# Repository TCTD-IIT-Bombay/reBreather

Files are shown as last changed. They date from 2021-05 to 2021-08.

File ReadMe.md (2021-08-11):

# Overview

There is currently an acute shortage of medical grade oxygen in large parts of India, as a consequence of a big surge in the number of critical Covid-19 cases, as well as logistical challenges associated with the oxygen supply chain. Several past and current students and research staff members of  [IIT Bombay](https://www.iitb.ac.in) (affiliated with [Tata Centre for Technology and Design](http://www.tatacentre.iitb.ac.in/), [Chemical Engineering](https://www.che.iitb.ac.in), and [Nex Robotics](http://www.nex-robotics.com)) have come together to attempt solutions which focus on reducing O<sub>2</sub> wastage, from the patient consumption perspective.

We have built a prototype breathing device called reBreather, which can minimize the wastage of oxygen when a patient is put on assisted breathing with supplemental oxygen via O<sub>2</sub> cylinders or centralised O<sub>2</sub> supply in hospitals.  Our reBreather prototype is a semi-closed circular breathing system that would allow patients to breathe in unused exhaled oxygen which has been filtered to remove CO<sub>2</sub>.

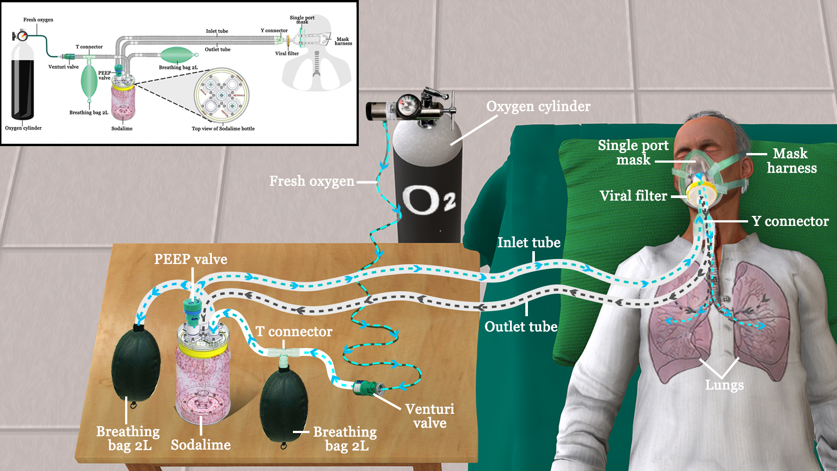
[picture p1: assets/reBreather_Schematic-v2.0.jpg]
reBreather Flow


The hardware design is available in the public domain under the Creative Commons 4.0 license ([CC BY-SA 4.0](https://creativecommons.org/licenses/by-sa/4.0/)) so that others can replicate the design. We urge individuals and makers communities across the world to come forward and 
1. Help assemble copies of the prototype, and 
2. Contribute design improvements or customizations, including for better scalability. 

This design has currently been tested on healthy volunteers: our objective in releasing this design now is to document the science behind the technique and test that it works in a practical context, and potentially help mitigate wastage of O<sub>2</sub> at a time when there is a heavy demand for it.

We have added explanations on how the reBreather works and on how to build a unit, with detailed pictures and instructions. Vendor and pricing details of the parts we have used in this design have also been provided. We have sourced these with relative ease in Mumbai; you may find cheaper - and better - alternatives for these items. Feel free to let us know if there are ways by which you can help us in improving the design or documentation, or with better vendor connections.  

# ⚠️ Disclaimers

We make no representation as to the operability and in particular, the fitness, safety, and efficacy of this solution. This prototype has been designed with inputs from experts with Anesthesiology and Intensive Care backgrounds, but at this time has only been informally tested on healthy volunteers. It has not been clinically tested in a controlled fashion and approved for routine use. We release this design into the public domain with the intent of encouraging further research and testing, towards improving the design. We strongly recommend the following:

- This prototype should only be tested and used under the close supervision of a trained medical professional, familiar with methods of alleviating respiratory distress.
- Flow settings should be modulated by systematic monitoring over time, by a professional, of a patient's FiO<sub>2</sub> (fraction of inspired oxygen), CO<sub>2</sub> percentage, and the effort of breathing.
- The prototype relies on the soda lime changing colour as its CO<sub>2</sub> absorption capacity is exhausted; its appearance must be frequently monitored, and the exhausted absorbent replaced with fresh soda lime in a timely fashion. 

# How does reBreather work?

In a normal open-loop oxygen-breathing system, a mask is directly connected to the oxygen supply at a particular flow rate. During inhalation, the human respiratory system takes in this oxygen stream, in some cases along with atmospheric air. In the exhalation cycle, the person breathes out unutilized gases as well as the CO<sub>2</sub> generated as a by-product of metabolism. A healthy person normally breathes in 5 liters per minute (L/min) of air. This corresponds (assuming air has ~20% O<sub>2</sub>) to about 1 L/min of O<sub>2</sub> being inhaled; of this, ~0.25 L/min of O<sub>2</sub> is consumed.  Critically ill Covid-19 patients can receive up to 50 L/min of O<sub>2</sub> using a high-flow nasal cannula and mask combination. Consequently, during one open loop breathing cycle for such patients, most of the oxygen is lost back to the atmosphere.

A rebreather is a closed (or semi-closed) loop system that helps the user to rebreathe the unused oxygen that they have just exhaled. To do this, rebreathers have a section that helps remove the CO<sub>2</sub> in the exhaled air thereby preventing an increase in the CO<sub>2</sub> concentration in the closed-loop system. The amount of oxygen absorbed by the user is replenished by a fresh supply of oxygen into the closed-loop. This concept has extensively been used in underwater diving breathing devices. Those designs are significantly more complex in practice, however, and have a fully closed loop system with air sensors measuring concentrations of O<sub>2</sub> and adjusting the input oxygen flow accordingly.

It will be beneficial to recirculate the unused oxygen, especially when the latter is in short supply.  Releasing a lot of oxygen results in the oxygen concentration going up, especially in closed spaces.  This could be a reason for the increased fire incidence in hospitals, during the current pandemic.  The solution presented in this work is an attempt to address this problem, as explained next.

Our solution (called reBreather) is a semi-closed circular breathing system. We have an inlet section which pumps in fresh oxygen from an oxygen cylinder or a centralised oxygen system in hospitals. The oxygen flow rate is set on the cylinder with a flow meter. An adjustable venturi valve is given at the input to allow for external air to be automatically pulled in based on the desired oxygen flow rate. A one port mask is attached to the patient; it has a Y connector which connects to a bacterial/viral filter at one end. At the other end, the Y connector has an inlet for incoming air and an outlet for exhaled air. Flow directions are regulated by using one-directional valves.  The exhaled air is fed to a container which contains medical-grade soda lime which selectively absorbs CO<sub>2</sub> and allows the rest of the air to pass through to the inlet section of our system.

Medical grade soda lime changes colour once it has exhausted its capability to absorb CO<sub>2</sub>. There are different indicator dyes in use, with colour change combinations varying across manufacturers and brands (for example, pink (fresh) to white (exhausted), or white (fresh) to violet (exhausted), etc.). It is important to note that a soda lime colour change must be promptly attended to: at this time we recommend that it be replaced with a fresh batch of soda lime towards continuous use of the device: an elevation in the CO<sub>2</sub> concentration in the rebreather circuit would be harmful to the patient.

Approximate calculations of unit performance are provided below for various scenarios. These are O<sub>2</sub> utilization estimates for a single patient, and assuming that a cylinder holds 7800 L of pure O<sub>2</sub>. The closed loop design assumes 10% purge of the recirculating stream, per cycle, with an equivalent introduction of fresh O<sub>2</sub>. Units are in cylinders/day.(Detailed calculations are available in a separate [pdf file](./assets/Estimated_Oxygen_Savings.pdf)).

| Scenario / cylinders per patient per day                                       | Open loop  | Closed loop  with reBreather |
|------------------------------------------------|:----------:|:----------------------------:|
| Nasal Cannula 6 L/min O<sub>2</sub> | 1.1 | 0.28 |
| Nonrebreathing mask (NRM), 15 L/min O<sub>2</sub> | 2.8 | 0.44 |
| High Flow Nasal Cannula (HFNC), 50 L/min O<sub>2</sub> | 9.2 | 1.09 |

# FAQs

1. Can I build this device based on the parts mentioned? \
Yes, you can. However, (as explained above) it should be used solely under the supervision of a trained medical professional. 

2. Is the design open source? \
Yes. The entire hardware design is made available in the public domain under a Creative Commons 4.0 license ([CC BY-SA 4.0](https://creativecommons.org/licenses/by-sa/4.0/)). This design is accessible on our [GitHub page](https://github.com/TCTD-IIT-Bombay/reBreather). 

3. How can I help? \
You can also help us in testing the design, and by suggesting modifications to further improve its performance and manufacturability. Talk to doctors and give us their inputs. There are several elements in the design which can be further optimised. Our primary focus during this initial build cycle has been on establishing efficacy of the design. We have, to a lesser extent, focussed on incorporating off the shelf branded parts which we think anyone else would also be able to source locally. Feel free to fork the project, edit it and create pull requests if you have a way to make the design better or have an alternate design which will work.
You can also help us (and others) by finding better vendor sources in your city.     

4. What is the current status of the project?  \
(As of Aug 11 2021:) We are releasing version v2.0 of the reBreather prototype design. This design has been tested on a healthy team member who was hooked up to a patient monitoring device, under the supervision of clinical specialists.  His vital signs, breathing rate, inhalation & exhalation O<sub>2</sub> /CO<sub>2</sub>  levels were monitored. \
At a low O<sub>2</sub>  input flow rate of 1 L/min, the volunteer was able to maintain normal breathing patterns with O<sub>2</sub>  and CO<sub>2</sub>  levels well within limits. We were able to establish that CO<sub>2</sub>  is continuously being removed from the system. \
A few changes were made on the v1.0 prototype design which includes adding another breathing bag after the venturi valve, changes in the design of the jar lid and the adapters to have a more efficient pathway to flow. Iterative experiments were also conducted on soda lime to test the amount of C0<sub>2</sub> absorbed and how to make it more long lasting. This version of prototype is now undergoing clinical trials.
There are further modifications that we are working on to make the designs better and easier to manufacture. We will keep updating the Hardware design folder with design variations as and when these changes are introduced.

5. How can I add modifications to the design? \
We urge you to contribute back any design updates. You can fork this  project (learn how to do so [here](https://www.youtube.com/watch?v=_NrSWLQsDL4)) and create a copy. Now create a new subfolder inside the Hardware Designs folder with the latest version number. The versioning scheme (**vX.Y**) is as follows: \
v1.0 --> Original Design \
v2.0 --> Updated Design \
For major modifications to a particular design, increment X by 1 (eg. v2.0, v3.0). If you make a minor edit to a particular design, increment Y by 1, from the base design you modified (eg. v1.2, v1.4, v2.3).\
In this new folder, make sure you have the following files and folders (For reference check the original v1.0 folder) 
- *Hardware Parts Explained.pdf* --> Explaining each and very part of your design with pictures 
- *Assembly Steps.pdf* --> Detailed steps on how you will put this together 
- *Bill of Materials* --> Bill of materials file containing the parts to be purchased/3D printed/Lasercut/moulded 
- *Mechanical CAD Folder* --> Containing editable files for the community along with the 3D printed files(if any)\
Detailing the changes made and why you think it is better. Add a picture of the full setup. List potential issues you find in the version you build so that others can help suggest improvements. 
Once the folder along with the above contents are made. Add the final picture of your setup to the main ReadMe file in the Hardware Designs folder with your version number so that someone can find the full design evolution in one page. \
Please submit a [pull request](https://docs.github.com/en/github/collaborating-with-issues-and-pull-requests/about-pull-requests) with your changes. We will review the changes and add to the Github project page.
6. How can I contact the team?  \
Drop us a mail at rebreather@tctd.iitb.ac.in

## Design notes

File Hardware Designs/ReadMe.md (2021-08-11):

# How to contribute to this project? 

We urge you to contribute and make the published designs better. You can fork this project(Learn [here](https://www.youtube.com/watch?v=_NrSWLQsDL4)) and create a copy of this project. Now create a new folder on the *Hardware Designs* folder with the latest version number. 

The versioning scheme (**vX.Y**) is as follows: 

v1.0 --> Original Design 
v2.0 --> Updated Design

For major modifications to a particular design, increment X by 1 (eg. v2.0, v3.0). If you make a minor edit to a particular design, increment Y by 1, from the base design you modified (eg. v1.2, v1.4, v2.3). 
In this new folder, make sure you have the following files and folders (For reference check the original v1.0 folder) 
- *Hardware Parts Explained.pdf* --> Explaining each and very part of your design with pictures 
- *Assembly Steps.pdf* --> Detailed steps on how you will put this together 
- *Bill of Materials* --> Bill of materials file containing the parts to be purchased/3D printed/Lasercut/moulded 
- *Mechanical CAD Folder* --> Containing editable files for the community along with the 3D printed files(if any) 
- *ReadMe.md* file --> Detailing the changes made and why you think it is better. Add a picture of the full setup. List potential issues you find in the version you build so that others can help suggest improvements. 

Once the folder along with the above contents are made. Add the final picture of your setup to the this ReadMe file towards the end in the Hardware Designs folder with your version number so that someone can find the full design evolution in one page. 

Please submit a [pull request](https://docs.github.com/en/github/collaborating-with-issues-and-pull-requests/about-pull-requests) with your changes. We will review the changes and add to the Github project page.

# Different Designs

### ***v1.0***

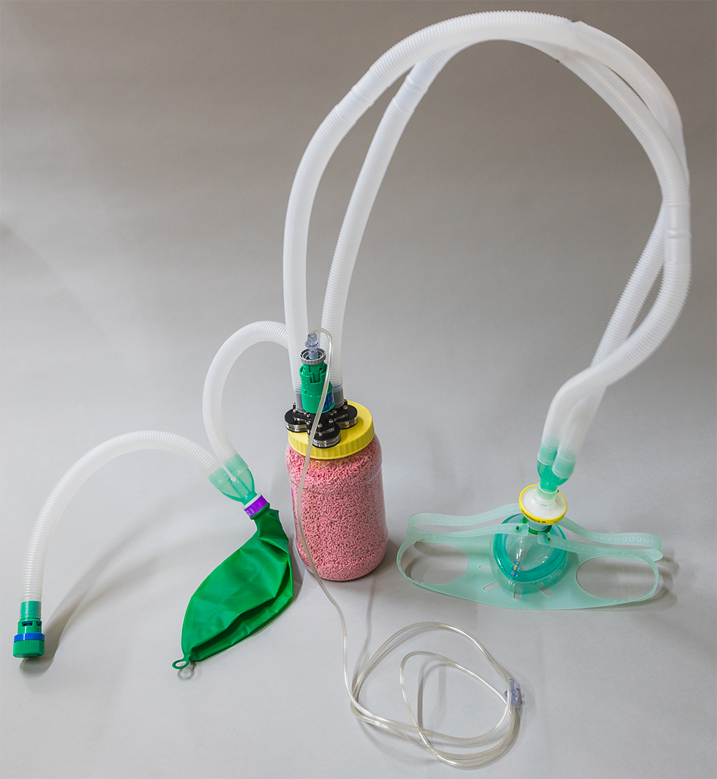
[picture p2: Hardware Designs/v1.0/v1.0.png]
v1.0


### ***v2.0***

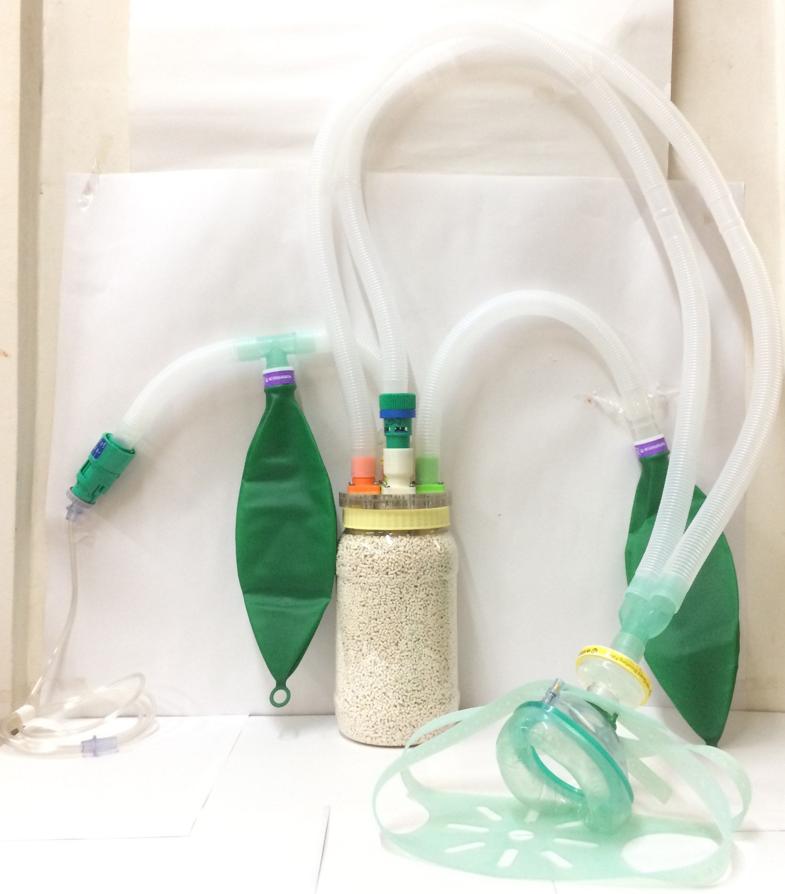
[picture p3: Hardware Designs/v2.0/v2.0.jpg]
v2.0


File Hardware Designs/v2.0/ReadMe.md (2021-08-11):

# Updated Design

The initial design was tested and a few changes were made, making the device more efficient and safe than the previous design. The changes will be mentioned below.

The usage of soda lime was also tested to bring out the maximum efficiency. Iterative experiments were carried out, by emulating the exhaled gas of a person with a CO<sub>2</sub> supplied to a container having the same amount of soda lime. The details of the experiment and the outcome is mentioned in the directory 'Sodalime'.

## Modifications in Design
- The valve have been brought out from the bottle lid, which allows easy replacement.
- An additional breathing bag is added after the venturi valve
- The PEEP outlet is coupled with exhalation port before entering the bottle to save wastage and better use of soda lime

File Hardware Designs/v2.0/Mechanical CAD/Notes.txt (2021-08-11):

Modification proposed:
1.Valve have been brought out from the bottle lid, allows easy replacement
2.Additional breathing bag to be added after venturi valve
3.It is better to use fixed venturi over adjustable venturi
4.Peep outlet is couple with exhalation port before entring the bottle to save wastage and better use of soda lime

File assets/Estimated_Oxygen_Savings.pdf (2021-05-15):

## Estimated O2 Savings by reBreather

The advantage of the Closed-Circuit system comes from the significant difference between the volume of O2 a patient with respiratory distress inhales and the actual volume of O2 the body picks up.

For reference, a healthy person breathes in ~5L/min of air (80% N2, 20% O2) which corresponds to ~1L/min of O2. Of this 1L/min inhaled, the healthy human body picks up only about
250mL/min [1] or 0.25L/min of O2. Hence the remaining 750mL/min of O2 is exhaled out unused and is lost to the environment. This O2 wastage can be more dramatic for ARDS patients: Covid-19 patients in intensive care can be given 50 L/min of O2 with only 1-1.5 L/min actually being utilized.

In a closed-circuit system, this lost oxygen is captured and recycled within the system. This allows the caregiver to send in fresh Oxygen only to make up for the O2 that is actually taken up by the human body.

A comparison of the number of cylinders consumed by a single patient when using non-closed-circuit systems like NRM/HFNO etc., versus our closed-circuit design is shown in the table below. The calculations for each of those numbers are shared after.

Scenarios | Open Loop (cylinders/day) | Closed Loop (10% purge) cylinders/day
Nasal Cannula, 6L/min* | 1.1 | ~0.28 (74% ↓)
Nonrebreathing mask, 15L/min* | 2.8 | ~0.44 (84%↓)
High Flow Nasal Cannula (HFNC), 50L/min* | 9.2 | ~1.09 (89%↓)

*Cylinder consumption shown for 1 patient

### 1 cylinder = 7800L of pure O2

## Scenarios:

### 1) Mild COVID patient treated at low-flow [6L/min O2] (Nasal Cannula)

Actual O2 Uptake by the body = 0.5L/min (assumed)

Open Loop:
O2 consumption from cylinder [L/min] = 6*60*24 = 8,640 L/day ~ 1.11 cyl/day

Closed Loop:
O2 consumption from cylinder [L/min] = 0.5*60*24 = 720 L/day ~ 0.09 cyl/day (without purge).
With 10% purge through a PEEP valve, this becomes 0.278 cyl/day.

### 2) Serious COVID Patient treated at 15L/min O2 (Nonrebreathing mask)

Actual O2 Uptake by the body = 1L/min (assumed)

Open Loop:
O2 consumption from cylinder [L/min] = 15*60*24 = 21,600 L/day ~ 2.77 cyl/day

Closed Loop:
O2 consumption from cylinder [L/min] = 1*60*24 = 1,440 L/day ~ 0.2 cyl/day. (without purge).
With 10% purge through a PEEP valve, this becomes 0.445 cyl/day.

### 3) Very Serious COVID Patient treated at 50L/min O2 (High flow nasal oxygen)

Actual O2 Uptake by the body = 1.5L/min (assumed)

Open Loop:
O2 consumption from cylinder [L/min] = 50*60*24 = 72,000 L/day ~ 9.23 cyl/day

Closed Loop:
O2 consumption from cylinder [L/min] = 1.5*60*24 = 2,160 L/day ~ 0.3 cyl/day (without purge).
With 10% purge through a PEEP valve, this becomes 1.09 cyl/day.

## References

[1] Leach RM, Treacher DF. The relationship between oxygen delivery and consumption. Dis Mon. 1994 Jul;40(7):301-68. PMID: 8020386.

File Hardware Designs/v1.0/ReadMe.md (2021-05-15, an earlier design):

# Initial Design

The initial design was done keeping prototyping time to a bare minimum and our goal was to document the science behind the technique and that it can actually work in real life. 

This design has been tested on a healthy team member who was hooked up to a patient monitoring device, under the supervision of clinical specialists.  His vital signs, breathing rate, inhalation & exhalation O<sub>2</sub> CO<sub>2</sub>  levels were monitored.

At a low O<sub>2</sub>  input flow rate of 1 L/min, the volunteer was able to maintain normal breathing patterns with O<sub>2</sub>  and CO<sub>2</sub>  levels well within limits. We were able to establish that CO<sub>2</sub>  is continuously being removed from the system.

## Known Issues
- The absorption process of C0<sub>2</sub> by sodalime is an exothermic reaction and the bottle will get warm during the process. We also tried pushing a large flow rate of pure C0<sub>2</sub> into the bottle and we did find that the PET bottle we used has a chance to get warped due to the heat. Potential alternatives are to pursue with thicker(2-3mm) acrylic tubes which has a higher deformation temperature. 
- The unidirectional valves do contain quite a number of parts which isn't that optimal for scalable designs. This is making the assembly process longer. We are working on simplifying the valve design significantly.

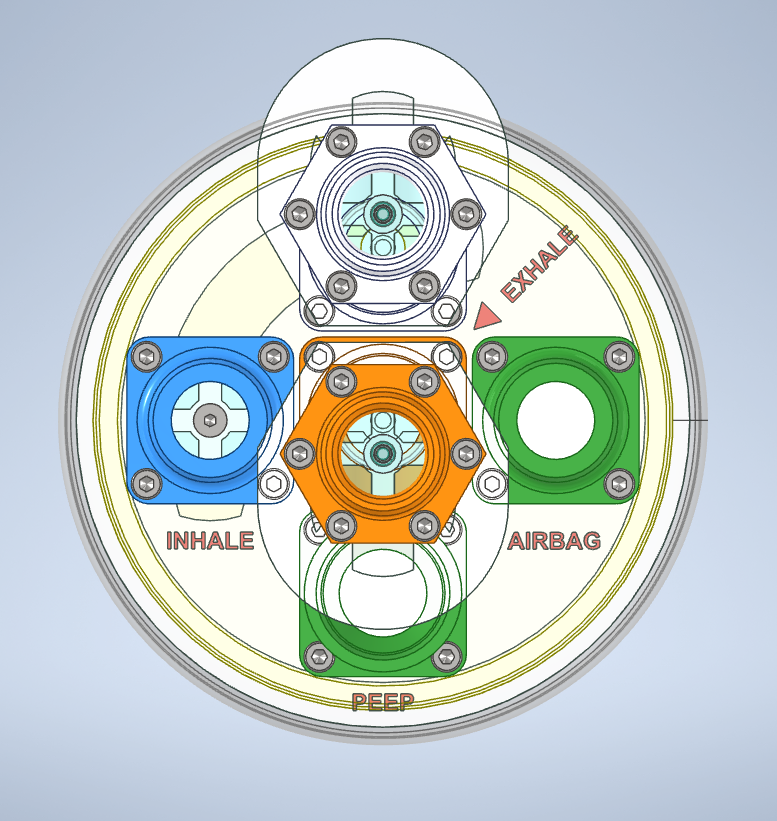
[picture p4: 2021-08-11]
Hardware Designs/v2.0/Mechanical CAD/Photos/Top.png

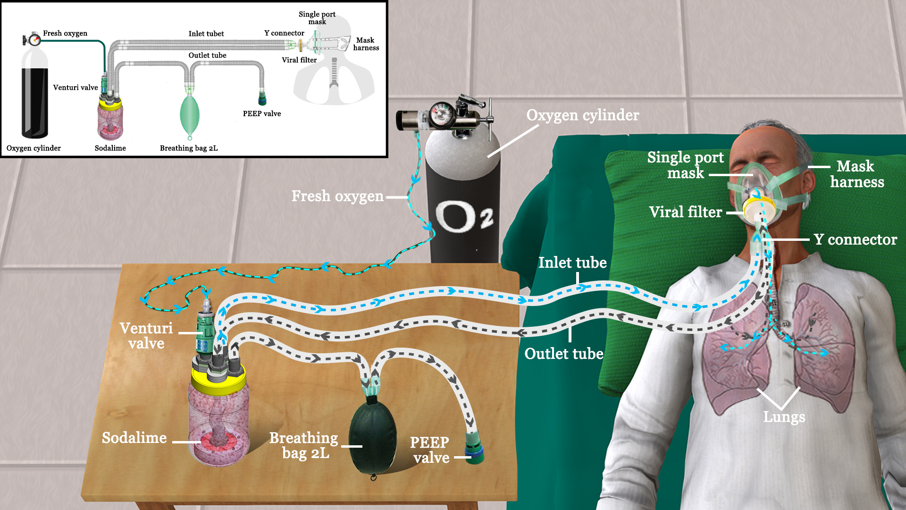
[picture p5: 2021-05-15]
assets/reBreather_Schematic-v1.0.jpg

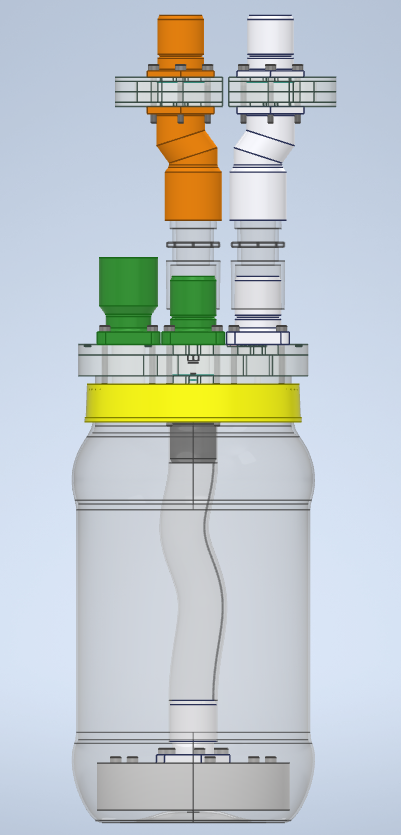
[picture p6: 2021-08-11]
Hardware Designs/v2.0/Mechanical CAD/Photos/Side_Right.png

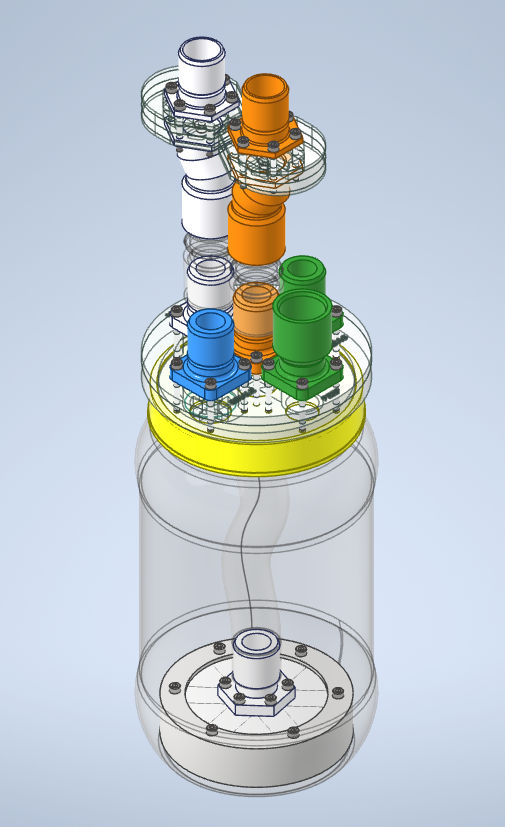
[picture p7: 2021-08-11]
Hardware Designs/v2.0/Mechanical CAD/Photos/Side_Iso.png

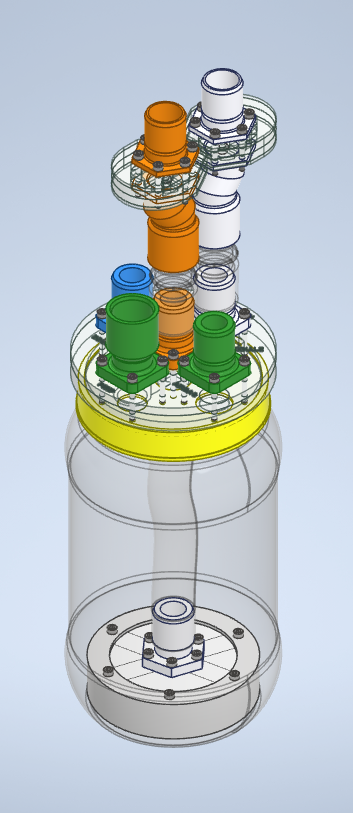
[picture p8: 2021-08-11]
Hardware Designs/v2.0/Mechanical CAD/Photos/Side_Iso_2.png

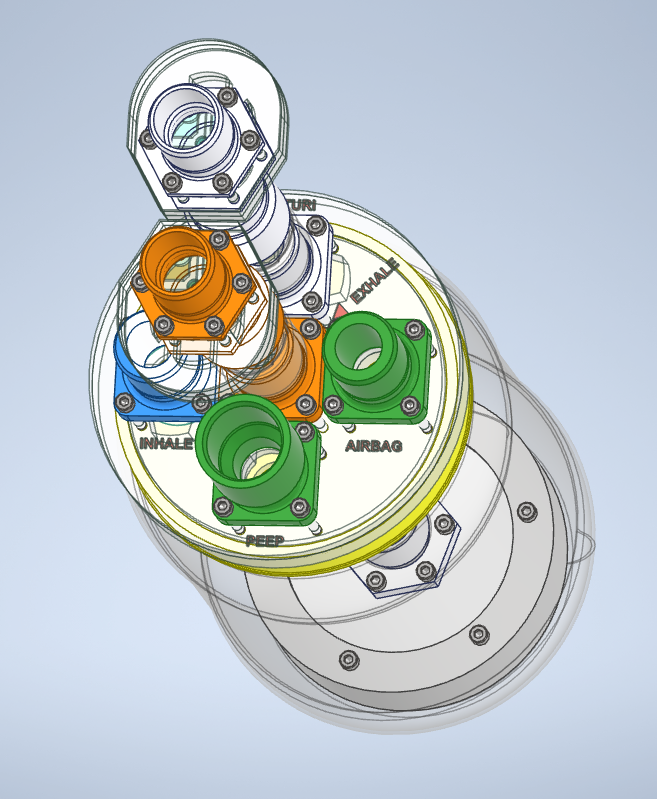
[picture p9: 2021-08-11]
Hardware Designs/v2.0/Mechanical CAD/Photos/Top_Iso.png

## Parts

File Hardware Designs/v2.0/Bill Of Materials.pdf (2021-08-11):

## Single Port Mask Design

Sl No. | Items | Qty | MRP Cost Bulk Cost | Comments
1 | O2 Inlet Tubing + Venturi Kit Set (1107085) | 1 | 403 | 130 | Multi Ox Venturi Mask kit(1117015) is preferred
2 | Viral Filter (1344007S) | 1 | 375 | 182 | Ports: Tube End 22M, Mask end 22F
3 | Y connector (1926000) | 1 | 360 | 250 | Price Assumed. All 3 ports are 22M
4 | T connector(1985000) | 1 | 360 | 250 | Price Assumed. Ports: 22M, 22M, 22F
5 | FlexTube Ventilator Tubing(2000000) - (Y connector + 1.6m x 2) | 1 | 795 | 250 | Tubing is 22F, Y connector is 22M
6 | Single Port Anaesthic Face Mask (1516000) | 1 | 1025 | 500 | Port: 22F
7 | CPAP Mask Harness (2224000) | 1 | 1200 | 560
8 | Adjustable PEEP Valve (2226000) | 1 | 2000 | 800 | Port: 22F
9 | Rebreathing Bag 2L (2820000 - 22F Neck) | 2 | 675 | 380 | Port: 22F Neck
10 | Directional valves (1921000 22M to 22F) | 2 | 720 | 500 | Near Venturi Valve and Exhaled air input to jar
11 | Intersob Plus Sodalime 5L Can (2180000) Pink to White or
| (2179000) White to Violet | 1 | 3200 | 1450 | Can be used for refilling 3 times
12 | Plastic Jar 2L | 1 | 100 | 100

On Outside: 3 Ports - 22M for exhaled gas tube input, 22F for filtered exhaled gas output, 22M for Peep valve(or 22F for 22M one way valve) On Inside: 2 Ports: Both 22M to connect tubing

## Total(INR) ₹ 11,213 ₹ 5,352

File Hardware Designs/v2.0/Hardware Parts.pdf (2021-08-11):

## reBreather Hardware Parts

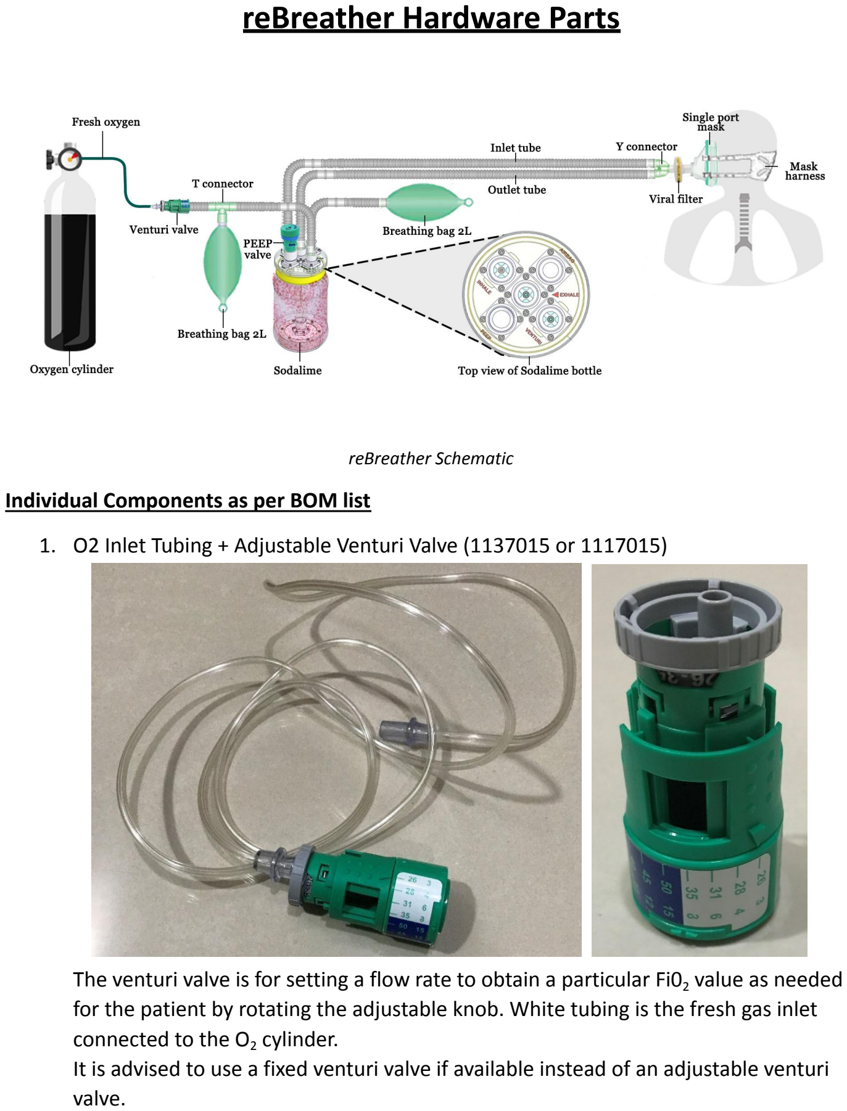
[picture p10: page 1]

reBreather Schematic

Individual Components as per BOM list

1. O2 Inlet Tubing + Adjustable Venturi Valve (1137015 or 1117015)

The venturi valve is for setting a flow rate to obtain a particular Fi02 value as needed for the patient by rotating the adjustable knob. White tubing is the fresh gas inlet connected to the O2 cylinder.
It is advised to use a fixed venturi valve if available instead of an adjustable venturi valve.

2. Viral Filter (1344007S)

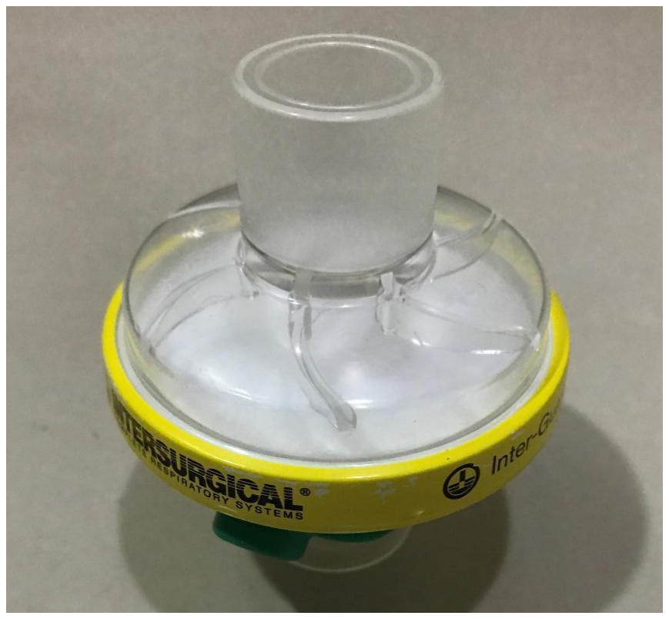
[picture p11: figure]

Acts as a filter to protect the patient from particulate matter. It has a filtration efficiency of 99.998%.

3. Y connector (1926000)

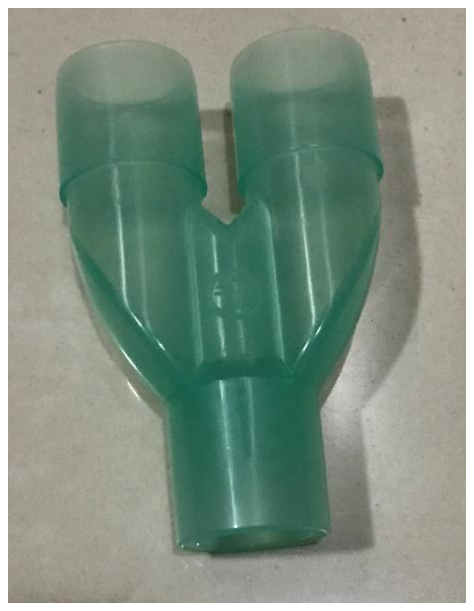
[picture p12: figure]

Y connector is for connecting the inlet and outlets tubings at the mask end.

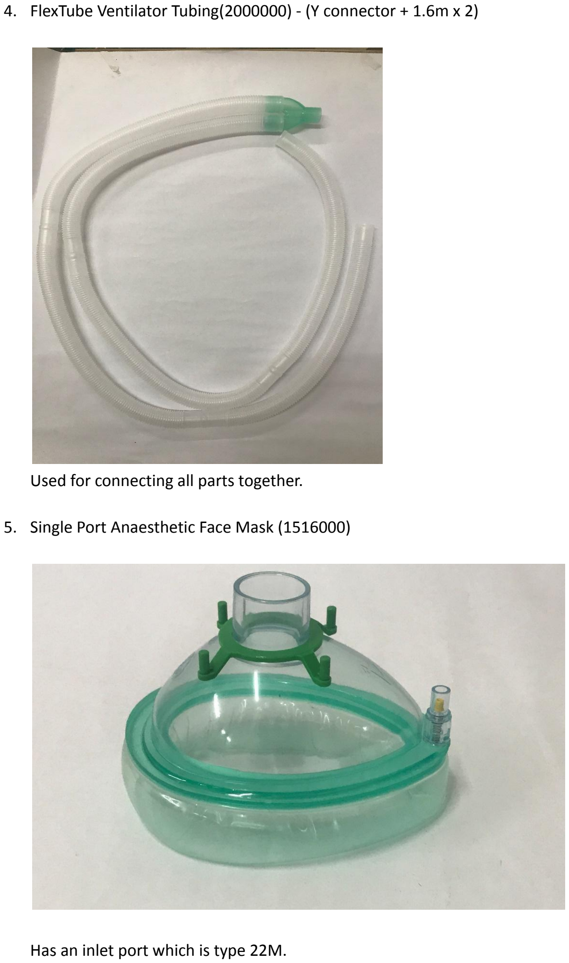
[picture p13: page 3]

4. FlexTube Ventilator Tubing(2000000) - (Y connector + 1.6m x 2)

Used for connecting all parts together.

5. Single Port Anaesthetic Face Mask (1516000)

Has an inlet port which is type 22M.

6. CPAP Mask Harness (2224000)

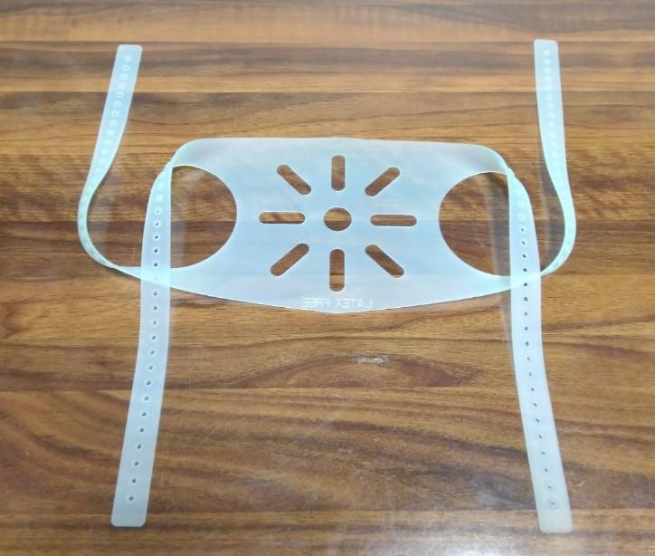
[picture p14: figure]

For tightly attaching the mask on the patient’s face without any gaps.

7. Adjustable PEEP Valve (2226000)

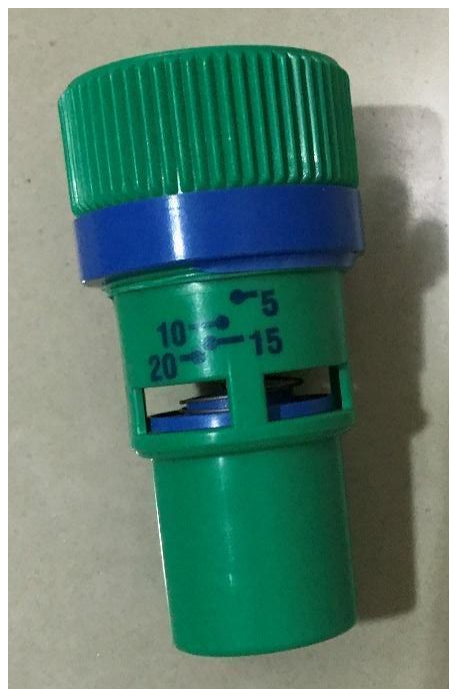
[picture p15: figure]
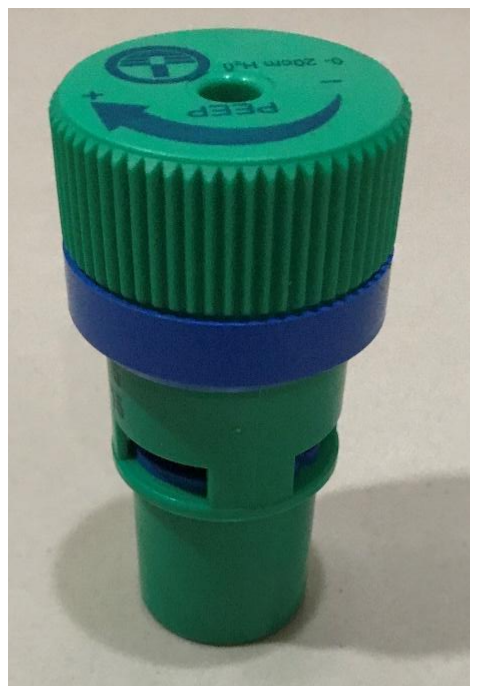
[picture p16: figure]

Positive end-expiratory pressure (PEEP) valve is an adjustable pressure valve to remove some air during the exhaust cycle. It needs to be set at a particular pressure value to maintain a certain pressure in the breathing circuit.

8. Rebreathing Bag 2L (2820000)

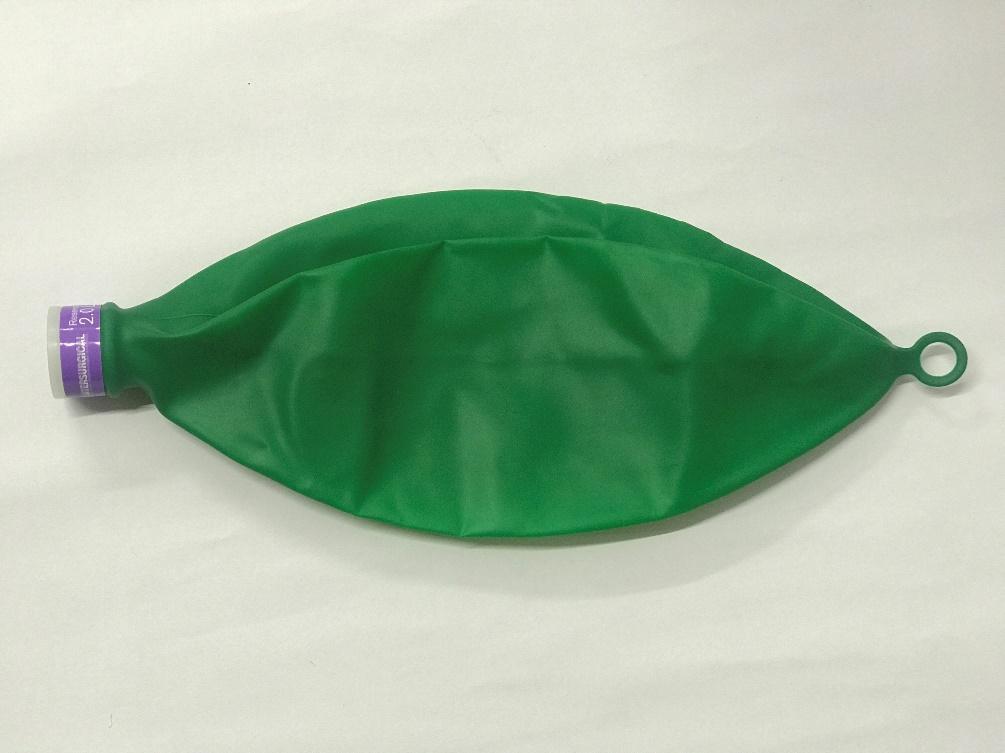
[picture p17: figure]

It’s a 2L Reservoir Bag to store air and also acts as a visual indicator of the patient’s breathing cycle by expanding and contracting.

9. Intersob Plus Sodalime 5L Can (2180000) Pink to White or (2179000) White to Violet


Soda lime is used for the absorption of CO2

in the exhaled air. It comes in various colour configurations. It changes its colour to indicate that the soda lime has exhausted itself by absorbing CO2 and that it needs to be replaced in the jar.
Common colour combos are pink(fresh) to white(exhausted) or white(fresh) to violet(exhausted). Please ensure that you replace the soda lime as its colour changes so that it can effectively filter CO2

. You can also shake the bottle once in a few hours to distribute the soda lime absorption evenly.

10. Plastic Jar 2L


The jar is used to store soda lime and acts as the filtration section of the reBreather.

11. Nuts and Bolts
For Bolts, we need M3 x 40mm x 18pcs, M3 x 15mm x 6pcs, M3 x 10mm x 15pcs For Nuts, we need M3 x 39pcs to attach the 3D printed parts together.
12. Fine Mesh Plastic Net (Approx 90mm diameter) – Qty 2


This can be repurposed from a fine mesh mosquito net or a plastic tea strainer. It helps in spreading the input exhaled air across the entire width of the jar. It will help in preventing the formation of caking/solidification of soda lime, which happens when airflow only goes through a particular route. It also needs to be attached to the top lid to prevent the soda lime from spilling over if the jar tips over on its side.

13. Circular Silicone Disc (Diameter: 26mm)


For making unidirectional valves

14. 3D printed Male Connector 22M Port


Used to connect various tubes on the jar.

15. 3D Printed Diffuser Bottom Cover, Diffuser Filter Holder, Diffuser Top Cover


These 3 parts together form the base of the jar and helps in aerodynamically spreading the exhaled air throughout the width of the can.

16. Acrylic Laser Cut Parts: Three discs with smaller cuts inside.


17. One Way Directional Valve 22M Flow in 22F Flow out - Intersurgical:


Also called as NRV or Non Return Valve

18. T connector ( T-piece 22M-22M/15F - 22F):


This T connector is used to connect breathing bag between venturi valve and external NRV

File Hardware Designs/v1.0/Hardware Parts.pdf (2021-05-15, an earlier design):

## reBreather Hardware Parts


reBreather Schematic

Individual Components as per BOM list

1. O2 Inlet Tubing + Adjustable Venturi Valve (1137015 or 1117015)

The venturi valve is for setting a flow rate to obtain a particular Fi02 value as needed for the patient by rotating the adjustable knob. White tubing is the fresh gas inlet connected to the O2 cylinder.

2. Viral Filter (1344007S)


Acts as a filter to protect the patient from particulate matter. It has a filtration efficiency of 99.998%.

3. Y connector (1926000)


Y connector is for connecting the inlet and outlets tubings at the mask end.


4. FlexTube Ventilator Tubing(2000000) - (Y connector + 1.6m x 2)

Used for connecting all parts together.

5. Single Port Anaesthetic Face Mask (1516000)

Has an inlet port which is type 22M.

6. CPAP Mask Harness (2224000)


For tightly attaching the mask on the patient’s face without any gaps.

7. Adjustable PEEP Valve (2226000)


Positive end-expiratory pressure (PEEP) valve is an adjustable pressure valve to remove some air during the exhaust cycle. It needs to be set at a particular pressure value to maintain a certain pressure in the breathing circuit.

8. Rebreathing Bag 2L (2820000)


It’s a 2L Reservoir Bag to store air and also acts as a visual indicator of the patient’s breathing cycle by expanding and contracting.

9. Intersob Plus Sodalime 5L Can (2180000) Pink to White or (2179000) White to Violet


Soda lime is used for the absorption of CO2 in the exhaled air. It comes in various colour configurations. It changes its colour to indicate that the soda lime has exhausted itself by absorbing CO2 and that it needs to be replaced in the jar.
Common colour combos are pink(fresh) to white(exhausted) or white(fresh) to violet(exhausted). Please ensure that you replace the soda lime as its colour changes so that it can effectively filter CO2. You can also shake the bottle once in a few hours to distribute the soda lime absorption evenly.

10. Plastic Jar 2L


The jar is used to store soda lime and acts as the filtration section of the reBreather.

11. Nuts and Bolts
For Bolts, we need M3 x 40mm x 18pcs, M3 x 16mm x 6pcs, M3 x 12mm x 15pcs For Nuts, we need M3 x 39pcs to attach the 3D printed parts together.
12. Fine Mesh Plastic Net (Approx 90mm diameter) – Qty 2


This can be repurposed from a fine mesh mosquito net or a plastic tea strainer. It helps in spreading the input exhaled air across the entire width of the jar. It will help in preventing the formation of caking/solidification of soda lime, which happens when airflow only goes through a particular route. It also needs to be attached to the top lid to prevent the soda lime from spilling over if the jar tips over on its side.

13. Circular Silicone Disc (Diameter: 26mm)


For making unidirectional valves

14. 3D printed Male Connector 22M Port


Used to connect various tubes on the jar.

15. 3D Printed Diffuser Bottom Cover, Diffuser Filter Holder, Diffuser Top Cover


These 3 parts together form the base of the jar and helps in aerodynamically spreading the exhaled air throughout the width of the can.

16. Acrylic Laser Cut Parts: Port Spacer, Valve Spacer, Valve Base Plate, Valve Top Plate, Net Filter Holder


These are used to make the unidirectional valves.

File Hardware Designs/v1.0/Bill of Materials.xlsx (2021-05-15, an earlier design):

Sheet: Purchased Parts
Sr.No. | Part Name | Description | Quantity | Comments/Links | Where to Purchase?
 |  |  |  |  | Vendor 1 |  |  | Vendor 2
 |  |  |  |  | Address & Contact Details | Total Price(INR)
 |  |  |  |  |  | MRP | Bulk | Address & Contact Details | Total Price(INR)
1 | O2 Inlet Tubing + Adjustable Venturi Valve (1137015 or 1117015) | For Oxygen Inlet and Air Mixing | 1 | Multi Ox Venturi Mask kit(1117015) is preferred but we have used 1137015 Port - 22F | A V Surgitech, Shop.No.23, Plot No-272 - 273, Hind Rajasthan Shopping Bhaudaji Road, Sion West, Sion , Mumbai - 400022 Kishor - 9137920335 022-24022999 | 260 | 130
2 | Viral Filter (1344007S) | Filtering inlet and outlet air to the patient | 1 | Ports: Tube End 22M, Mask end 22F | A V Surgitech | 375 | 182
3 | Y connector (1926000) | As a coupler to connect inlet and outlet tubes on the single port mask | 1 | All 3 ports are 22M | A V Surgitech | 360 | 250
4 | FlexTube Ventilator Tubing(2000000) - (Y connector + 1.6m x 2) | Tubing to connect parts | 1 | Tubing is 22F, Y connector is 22M | A V Surgitech | 795 | 250
5 | Single Port Anaesthetic Face Mask (1516000) | Single port Mask | 1 | Ports: 22M - Inlet | A V Surgitech | 1025 | 500
6 | CPAP Mask Harness (2224000) | To fit the mask tightly to the patient | 1 |  | A V Surgitech | 1200 | 560
7 | Adjustable PEEP Valve (2226000) | Adjustable Pressure valve to remove air during the exhaust cycle | 1 | Port: 22M | A V Surgitech | 2000 | 800
8 | Rebreathing Bag 2L (2820000 ) | Reservoir Bag as buffer | 1 | Port: 22F Neck | A V Surgitech | 675 | 380
9 | Intersob Plus Sodalime 5L Can (2180000) Pink to White or (2179000) White to Violet | Sodalime for Co2 Removal from the system | 1 |  | A V Surgitech | 3200 | 1450
10 | Plastic Jar 2L | Container for holding sodalime | 1 | On Outside: 4 Ports (3 ports with directional valves) - All 22M On Inside: 2 Ports: Both 22M to connect tubing | Amazon (https://www.amazon.in/Sunpet-Premium-Round-Jar-Spl2000-04/dp/B017K0LQ5K) | 100 | 100
11 | Bolts | Fastening the 3D printed ports to the lid cover and diffuser | 39 | M3 x 40mm x 18pcs M3 x 16mm x 6pcs M3 x 12mm x 15pcs | Local Hardware shop | 75 | 75
12 | Nuts |  | 39 | M3 x 39pcs | Local Hardware shop
13 | Fine mesh Plastic Net (Approx 90mm diameter) | To spread the incoming air throughout the width of the can. To prevent caking of sodalime | 2 | Repurpose from a fine mesh mosquito net or plastic tea strainer | Local Hardware shop | 30 | 30
14 | Circular silicone disc | For making unidirectional valves | 3 | Diameter - 26mm. Currently repurposed from N95 masks with valves | Local Medicalshop for N95 masks. Need to find a proper vendor who makes silicone discs | 75 | 75
 |  |  |  |  | Total (INR) | 10170 | 4782

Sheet: 3D PrintLaser Cut Parts
3D Printed Parts
Sl No | Part Name | Description | Quantity | Material | Approx 3D Print Time(in mins) Infill 100% | Comments/Links
1 | Diffuser_Bottom_Cover | To close the plastic mesh assembly | 1 | ABS or PLA | 200 mins
2 | Diffuser_Filter_Holder | To hold the plastic mesh on to the ring | 1 | ABS or PLA | 125 mins
3 | Diffuser_Top_Cover | To hold plastic mesh in the assembly | 1 | ABS or PLA | 180 mins
4 | Male_Adapter_Port_22M | Ports on the jar for various connections | 6 | ABS or PLA | 120 mins each
Laser Cut Acrylic Parts
Sl No | Part Name | Description | Quantity | Material | Thickness | Comments/Links
1 | Port_Spacer | Used as spacers in the valve design | 4 | Acrylic | 5 mm
2 | Valve_Spacer | To be used in betwen Valve_Base_Plate and Valve_Top_Plate parts | 6 | Acrylic | 5 mm
3 | Valve_Base_Plate | Valve sits on this plate | 3 | Acrylic | 2 mm
4 | Valve_Top_Plate | It keeps valve in place using nut and a bolt | 3 | Acrylic | 2 mm
5 | Net_Filter_Holder | To hold the Net filter kept at bottom on container lid | 3 | Acrylic | 2 mm

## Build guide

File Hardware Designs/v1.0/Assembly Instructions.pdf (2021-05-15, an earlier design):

## reBreather Assembly Instructions

Before starting the assembly process, please ensure that you have all the items mentioned in the BOM which are to be purchased, 3D printed and Laser Cut.

### 1. Jar Lid Modifications

- Take the jar lid and drill holes of 3mm diameter to fit your M3 bolts.
- Draw lines to find the midpoint of the 6 holes.
- Drill a hole of 13mm diameter for airflow at the centre. Repeat this for all 4 holes.
- Make the same pattern holes on the net as well to fix it inside the section of the lid.

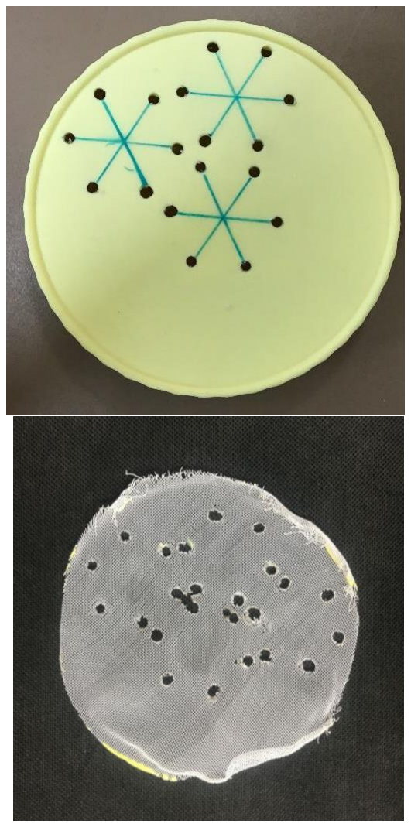
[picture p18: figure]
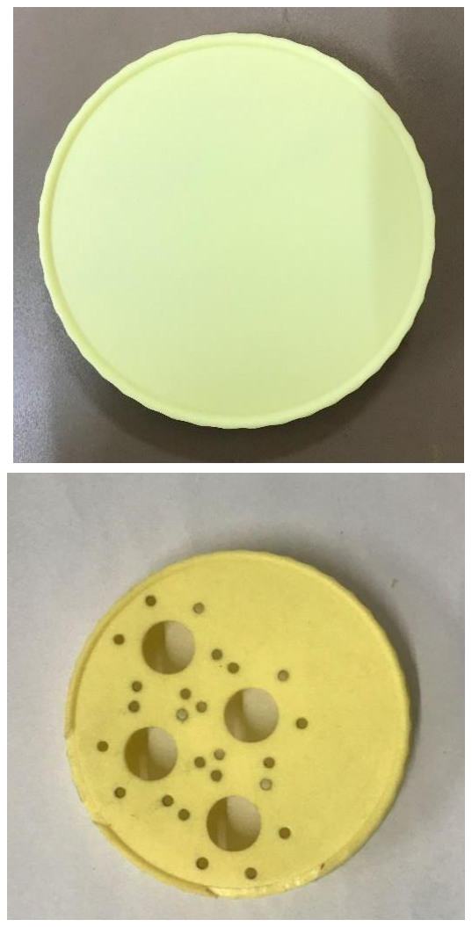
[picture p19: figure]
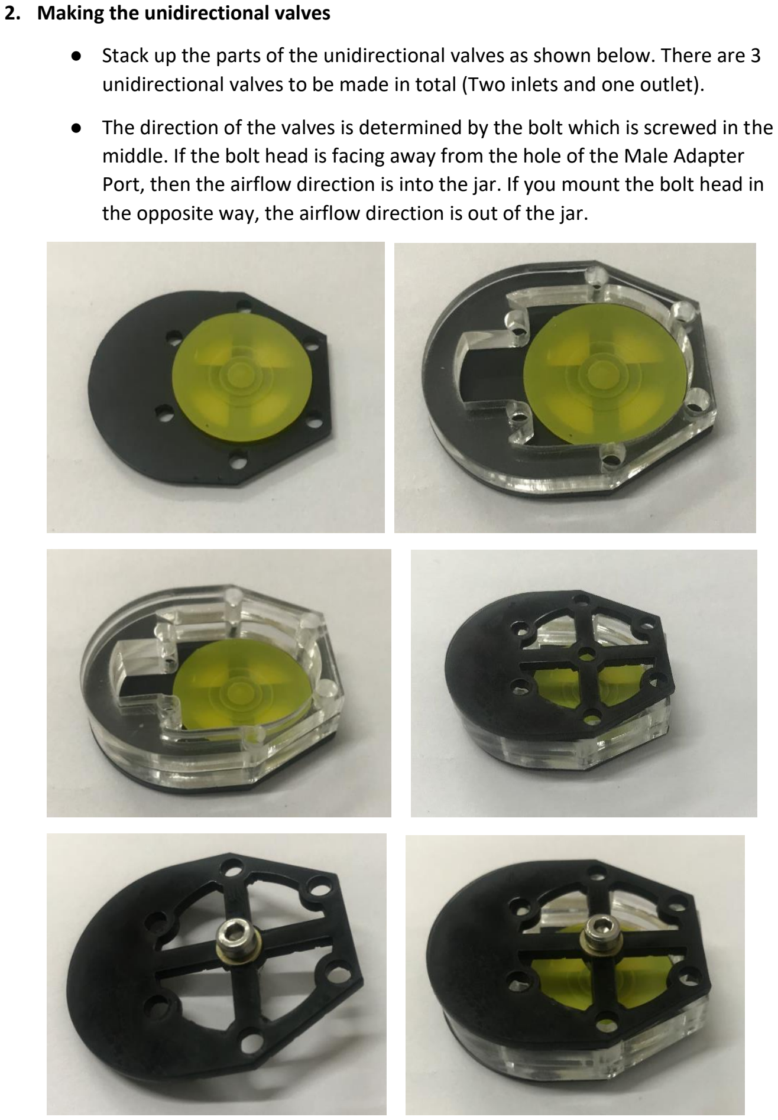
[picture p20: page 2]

### 2. Making the unidirectional valves

- Stack up the parts of the unidirectional valves as shown below. There are 3 unidirectional valves to be made in total (Two inlets and one outlet).
- The direction of the valves is determined by the bolt which is screwed in the middle. If the bolt head is facing away from the hole of the Male Adapter Port, then the airflow direction is into the jar. If you mount the bolt head in the opposite way, the airflow direction is out of the jar.

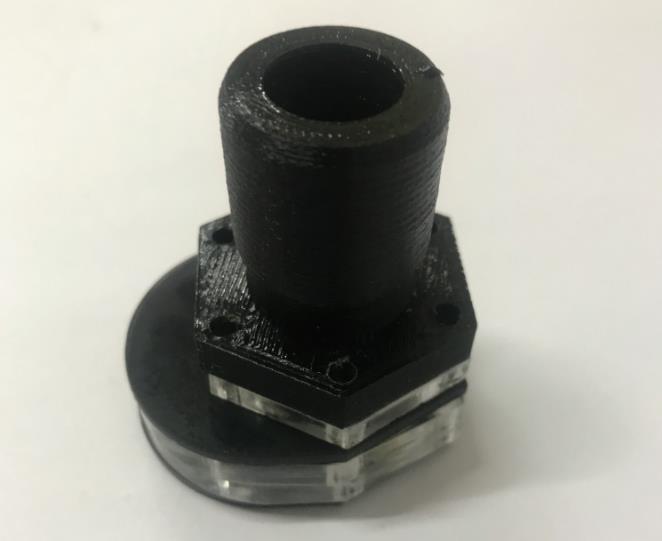
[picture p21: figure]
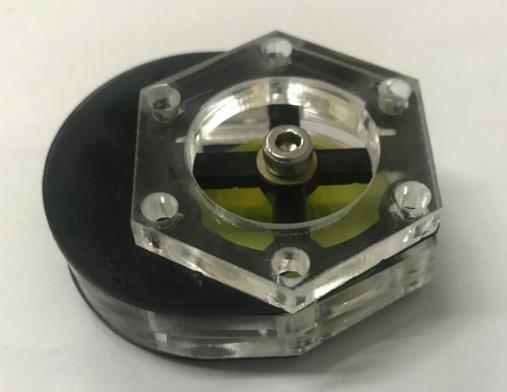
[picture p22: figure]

Use Transparent Acrylic for all the parts (In pictures we used black because of resource constraints due to lockdown)

### 3. Fixing connectors to Jar lid

- Screw the three unidirectional Ports and one Male Adapter Port to the top of the lid. Of the three unidirectional Ports, two of them allow air into the jar and one allows air to move out of the jar.
- Add the net and Hexagonal Net Filter Holder below the lid before screwing the nut in position.
- On the centre hole, after connecting the unidirectional valve make sure to connect a male connector on the bottom of the lid. Make sure both top and bottom male connectors are in line.

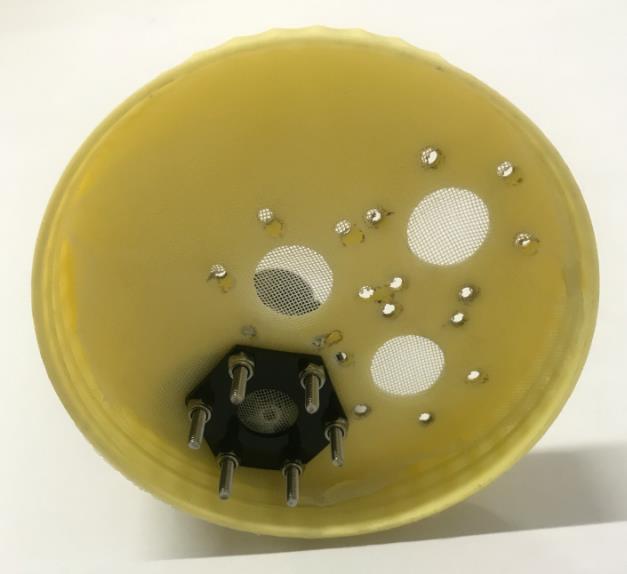
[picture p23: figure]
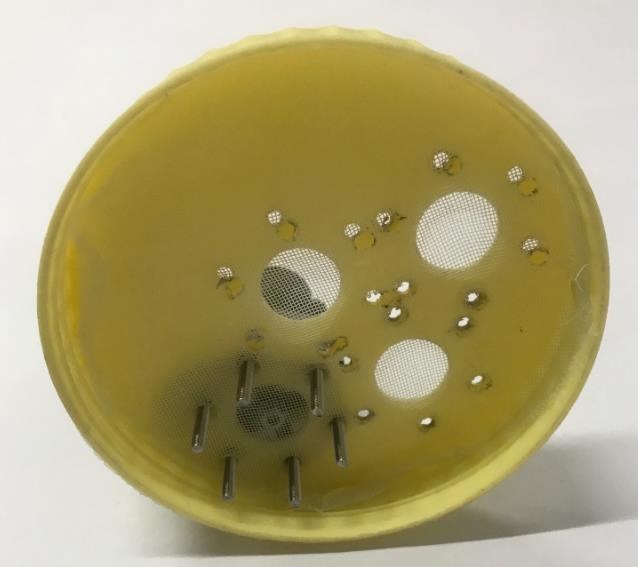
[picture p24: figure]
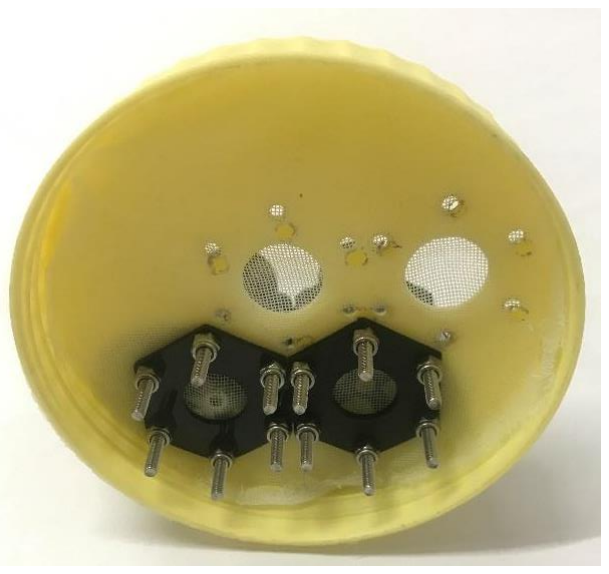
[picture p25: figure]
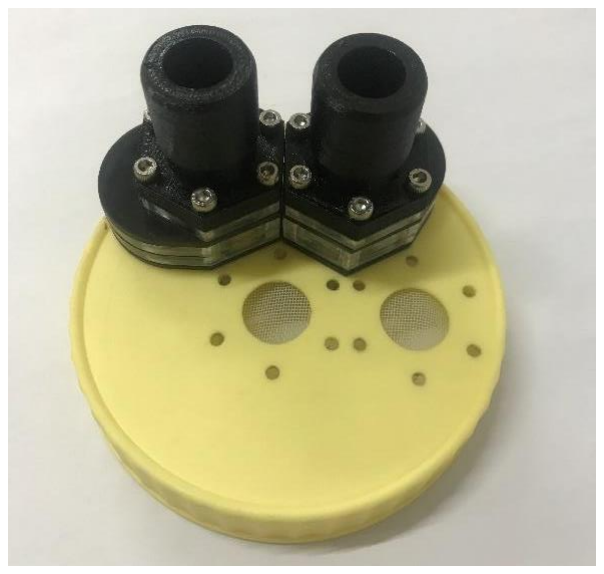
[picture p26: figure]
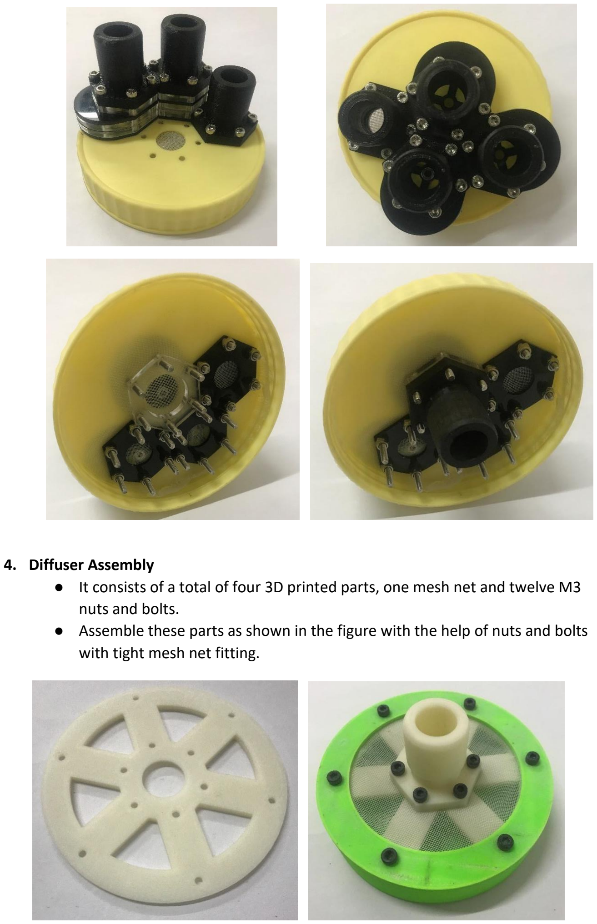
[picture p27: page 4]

### 4. Diffuser Assembly

- It consists of a total of four 3D printed parts, one mesh net and twelve M3 nuts and bolts.
- Assemble these parts as shown in the figure with the help of nuts and bolts with tight mesh net fitting.

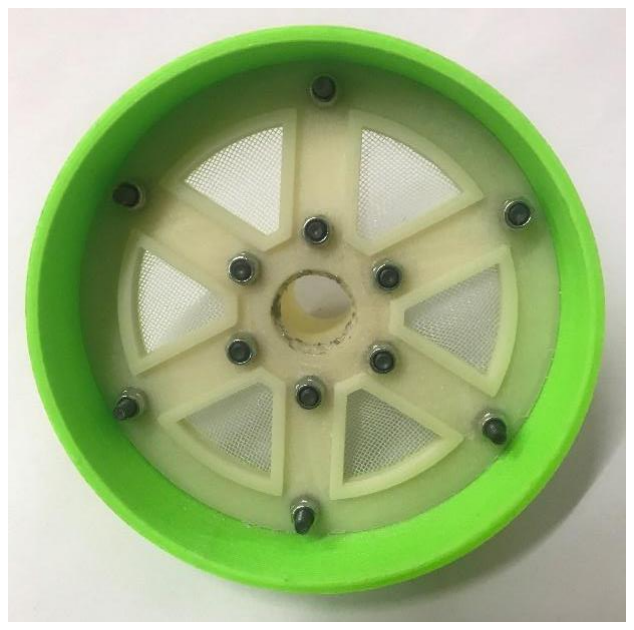
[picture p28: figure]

### 5. Cutting Ventilator Tubing

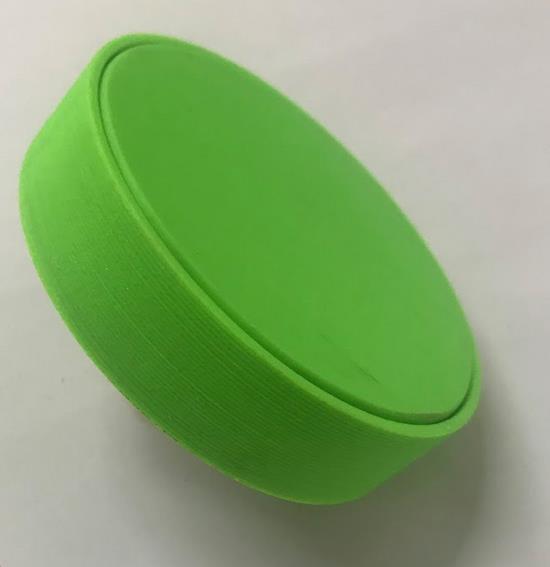
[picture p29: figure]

- Cut the ventilator tubing as mentioned at the following spots. The two smaller sections are used to connect the PEEP valve, tubing inside the jar and the rebreather bag.
- Please ensure that each numbered section of the tube goes to its respective position to ensure the optimal usage of tubes in a package.
- Cut Section 8 into 2 parts.
- Use the 16.5 cm part to connect two male ports inside the Jar i.e. one port below the lid and the on the diffuser part. The 24.5cm part is used later to connect the PEEP valve to the rebreather bag.

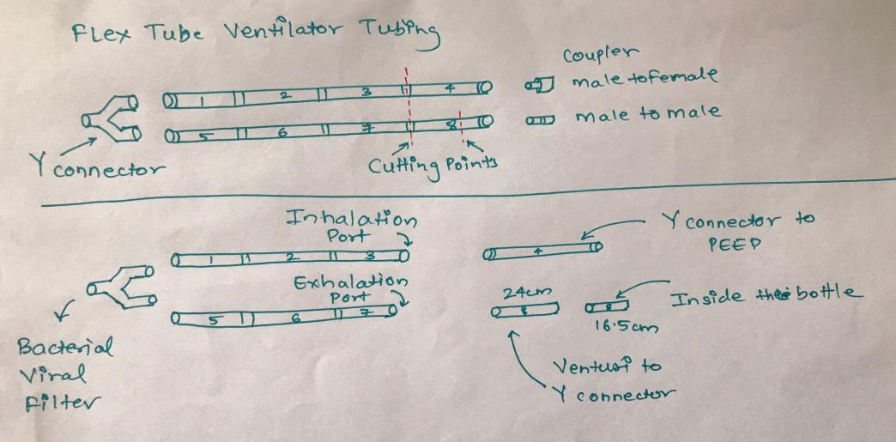
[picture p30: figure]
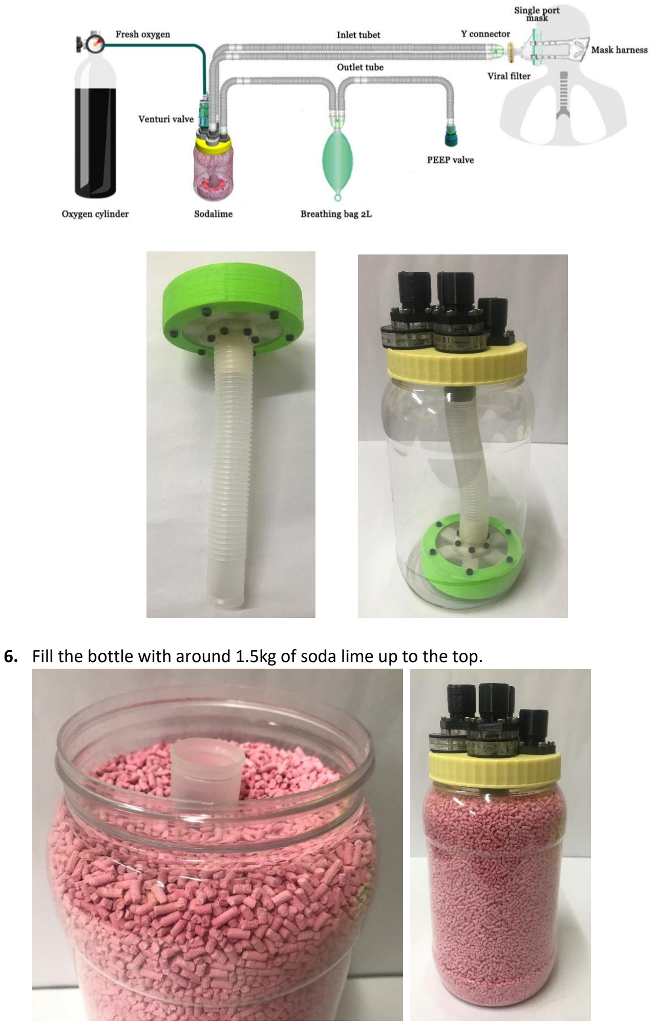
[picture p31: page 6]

6. Fill the bottle with around 1.5kg of soda lime up to the top.

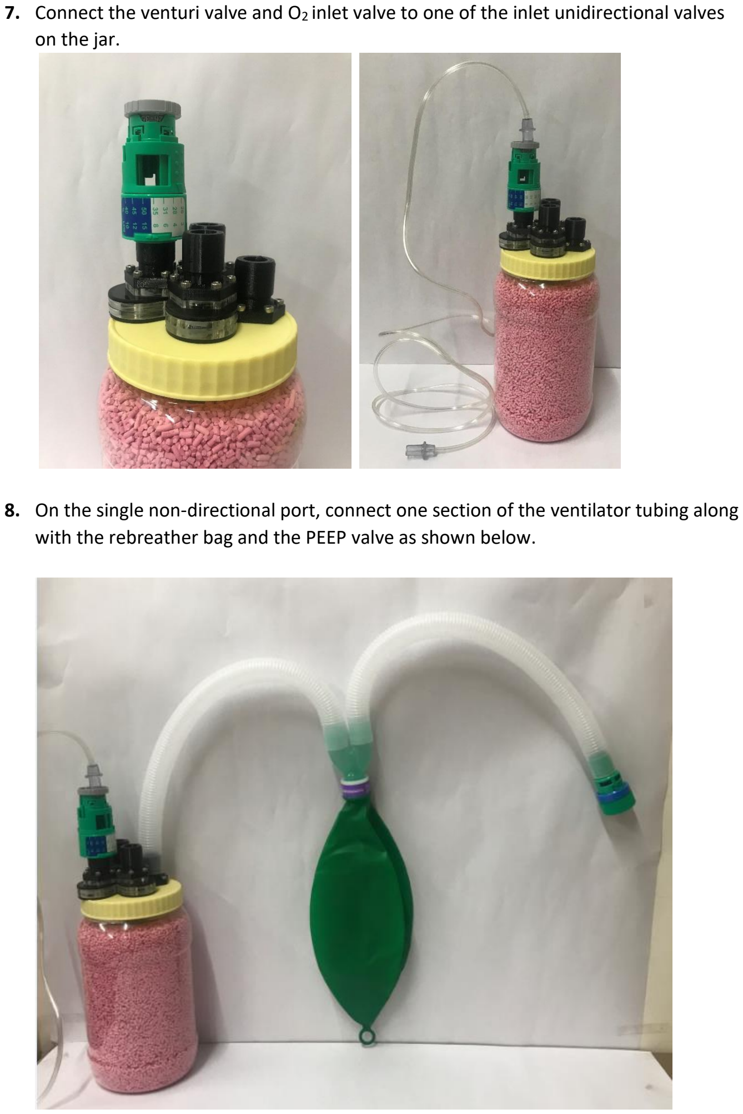
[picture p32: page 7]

### 7. Connect the venturi valve and O2 inlet valve to one of the inlet unidirectional valves

on the jar.

### 8. On the single non-directional port, connect one section of the ventilator tubing along

with the rebreather bag and the PEEP valve as shown below.

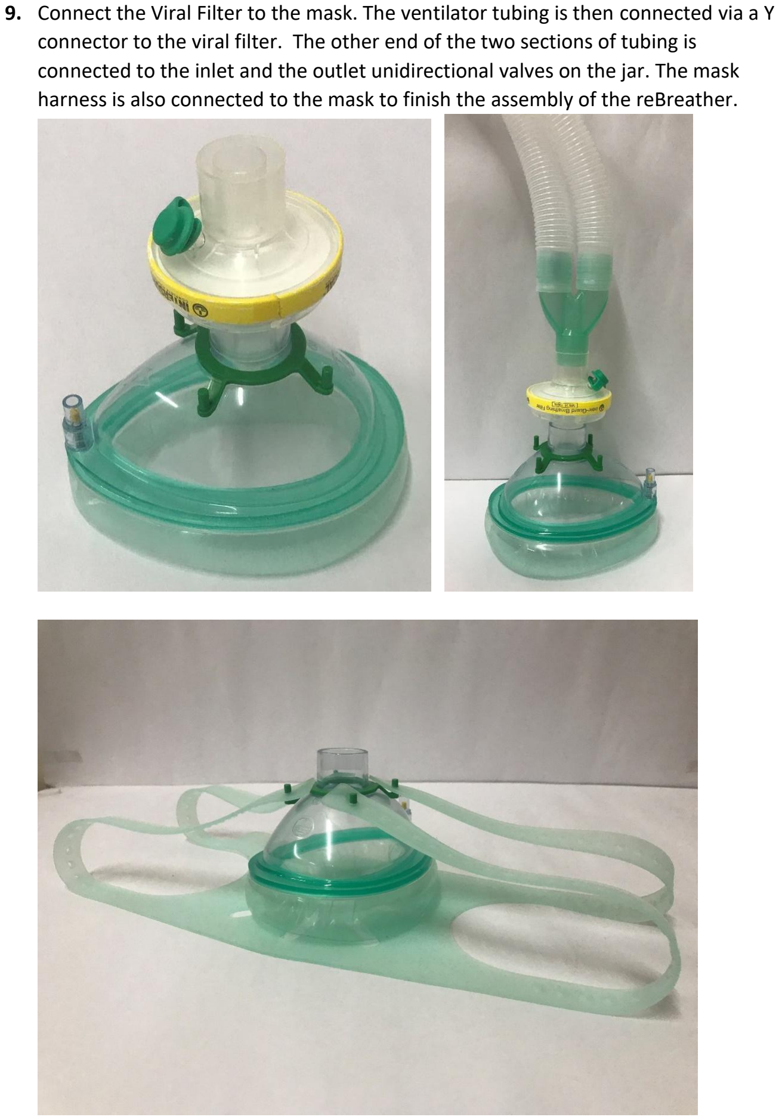
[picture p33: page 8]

### 9. Connect the Viral Filter to the mask. The ventilator tubing is then connected via a Y

connector to the viral filter. The other end of the two sections of tubing is connected to the inlet and the outlet unidirectional valves on the jar. The mask harness is also connected to the mask to finish the assembly of the reBreather.

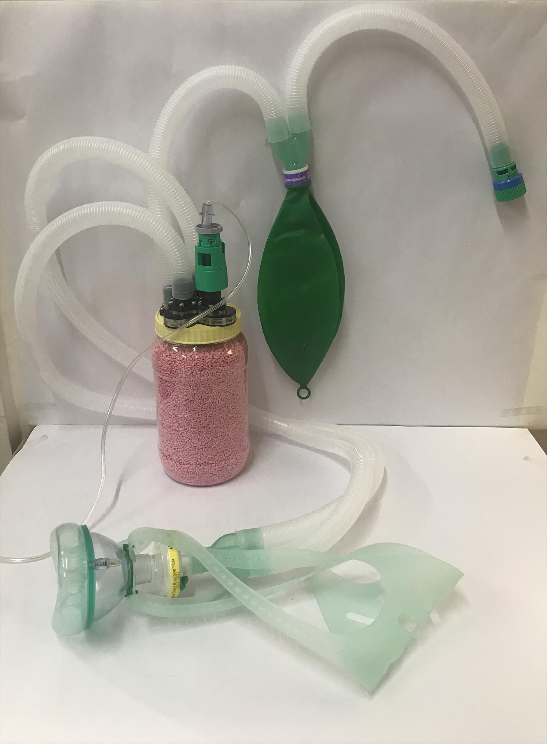
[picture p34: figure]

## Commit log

2021-05-15 Adding Mechanical Design Files
    [Connecting Pipe.x_b, Connecting pipe.FCStd, Container Lid.FCStd, Container Lid.x_b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]
2021-05-15 Adding Bill of Materials
    [Bill of Materials.xlsx]
2021-08-11 Adding Updated Assembly Instructions
2021-08-11 Updated Bill of Materials
2021-08-11 Adding Updated Designs
    [22M_Airbag_Port_Green.FCStd, 22M_Airbag_Port_Green.igs, 22M_Airbag_Port_Green.ipt, 22M_Airbag_Port_Green.stl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]
